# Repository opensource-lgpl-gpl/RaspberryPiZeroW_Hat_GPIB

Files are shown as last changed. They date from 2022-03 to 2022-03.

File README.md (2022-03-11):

# RaspberryPiZeroW_Hat_GPIB
## A $25.66 Dongle 
### Alternative to GPIB National Instrument's USB-GPIB-HS (MSRP: $1,476) and Prologix GPIB-LAN (MSRP: $189.99): 
This is used to standardize old Lab Instruments (Ammeters and Voltage Sources) like the Kiethley Picoammeter and Voltage Source so that a computer can connect wired via USB-A or wirelessly via bluetooth to a Raspberry Pi Zero with Wifi capabilities. 

This contraption RaspberryPiZeroW_Hat_GPIB can deliver results wirelessly via bluetooth or wired via USB-A (Plug) to USB (Plug) so that results can be delivered wirelessly in order to support work-from-home pandemic initiatives. 

This allows the older lab instruments to have the same capabilities as newer more expensive lab instruments that can cost thousands of dollars. 

This side-project used free and open-source tools to show: 
- Free software like KiCAD can completely replace Altium and intra-convertibility between Altium-to-KiCAD. 
- Free software auto-routing tool FreeRoute can replace most of manual PCB design routing. 
- Free software FreeCAD can completely replace SolidWorks, AutoCAD, et cetera (all costly "CAD" software). 

## Why was this created? 
During my time at NASA, I was tasked with getting a Prologix-LAN (MSRP $189.99) to talk to an old lab instrument: 

I was having a hard time connecting to a Prologix GPIB-Lan that was talking to a Kiethley instrument because when I sent the Prologix controller a command to go into "recieve"/"listen" mode, the logic was inverted; what resulted was the Prologix controller started to spew out a lot of data. Then when I wanted the Prologix controller to give me data or in other words, to "talk," the Prologix controller was silenced and went into "recieve"/"listen" mode. 

So I said to myself: "Why would I want to use a GPIB controller that does the exact opposite of what you want it to? Wouldn't that unpredictability potentially compromise valuable results someday when something invariably goes wrong, and you are trying to look for a root-cause?"

To me, this was not rocket science; I scoured the internet and found Thomas Klima's work on Raspberry Pi Model 3's USB-GPIB. 

Link to thesis paper (I studied German at University of Freie-Universitat, Berlin, Germany in 2013): http://elektronomikon.org//Bakkarbeit%20RasPi-GPIB%20Thomas%20Klima.pdf

I worked on this project about 6-8 hours total; most of the time was spent on tool setup and getting used to KiCAD, FreeCAD, and FreeRoute on a Mac machine.

This $25 dongle RaspberryPiZeroW_Hat_GPIB would be placed on every old lab instrument to modernize/"upgrade" it. 

## Bill of Materials from Digikey and OshPark and Raspberry Pi 
### (Total Cost of Materials)
| Part                               | Unit price  | Quantity | Digikey Part No.    | Price    |
| ---------------------------------- | ----------- | -------- | ------------------- | -------- |
| IC TRANSCEIVER HALF 8/8 20DIP      | 3.69        | 1        | SN75160BN           | $3.69    |
| IC TRANSCEIVER HALF 8/8 20SOIC     | 2.74        | 1        | SN75161BDWR         | $2.74    |
| RES ARRAY 5 RES 3.3K OHM 10SIP     | 0.63        | 2        | 4610X-102-332LF     | $1.26    |
| RES ARRAY 9 RES 6.8K OHM 10SIP     | 0.63        | 2        | 4610X-101-682LF     | $1.26    |
| CAP CER 0805 220NF 100V X7R 5%     | 0.31        | 1        | C0805C224J1REC7800  | $0.31    |
| RES 100 OHM 1% 1/4W 0805           | 0.07        | 20       | RNCP0805FTD100R     | $1.40    |
| Oshpark PCB Fab                    | $5.00       | 1        | N/A                 | $5.00    |
| Raspberry Pi   Zero W              | $10.00      | 1        | N/A                 | $10.00   |
|                                    |             |          | **Total:**          | $25.66   |

## PCB design and schematics. 
### Tool used: KiCAD
#### Cost of Tool used: Free, Open-source
KiCAD is a free alternative to more expensive software suites like Altium. 


## FreeRouting Tool to auto-route the PCB
### Tool used: FreeRouting
#### Cost of Tool used: Free, Open-source
I used the open-source and free tool called FreeRouting (https://freerouting.org) to route the PCB and ensure that a mounting bracket would fit. 

The PCB was designed using Free Routing to prevent cross-talk of wires as well as support a FreeCAD-designed mounting bracket. 

What is shown is the schematics taken from KiCAD. 



## Right Angle Mounting Bracket between the Raspberry Pi Zero W and GPIB Rpi Hat. 
### Tool used: FreeCAD
#### Cost of Tool used: Free, Open-source
This is the mounting bracket that was to be 3D printed using my personal 3D Printer from Monoprice. 


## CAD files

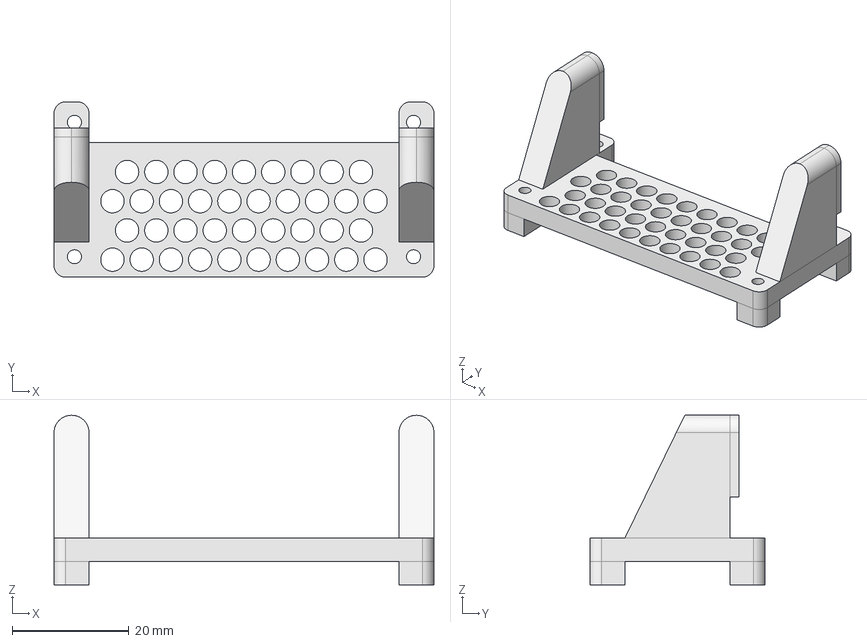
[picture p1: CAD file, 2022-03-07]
Mounting Bracket - FreeCAD/Mounting Bracket.FCStd
65.0 x 30.0 x 29.0 mm

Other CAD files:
Mounting Bracket - FreeCAD/Mounting Bracket.stl

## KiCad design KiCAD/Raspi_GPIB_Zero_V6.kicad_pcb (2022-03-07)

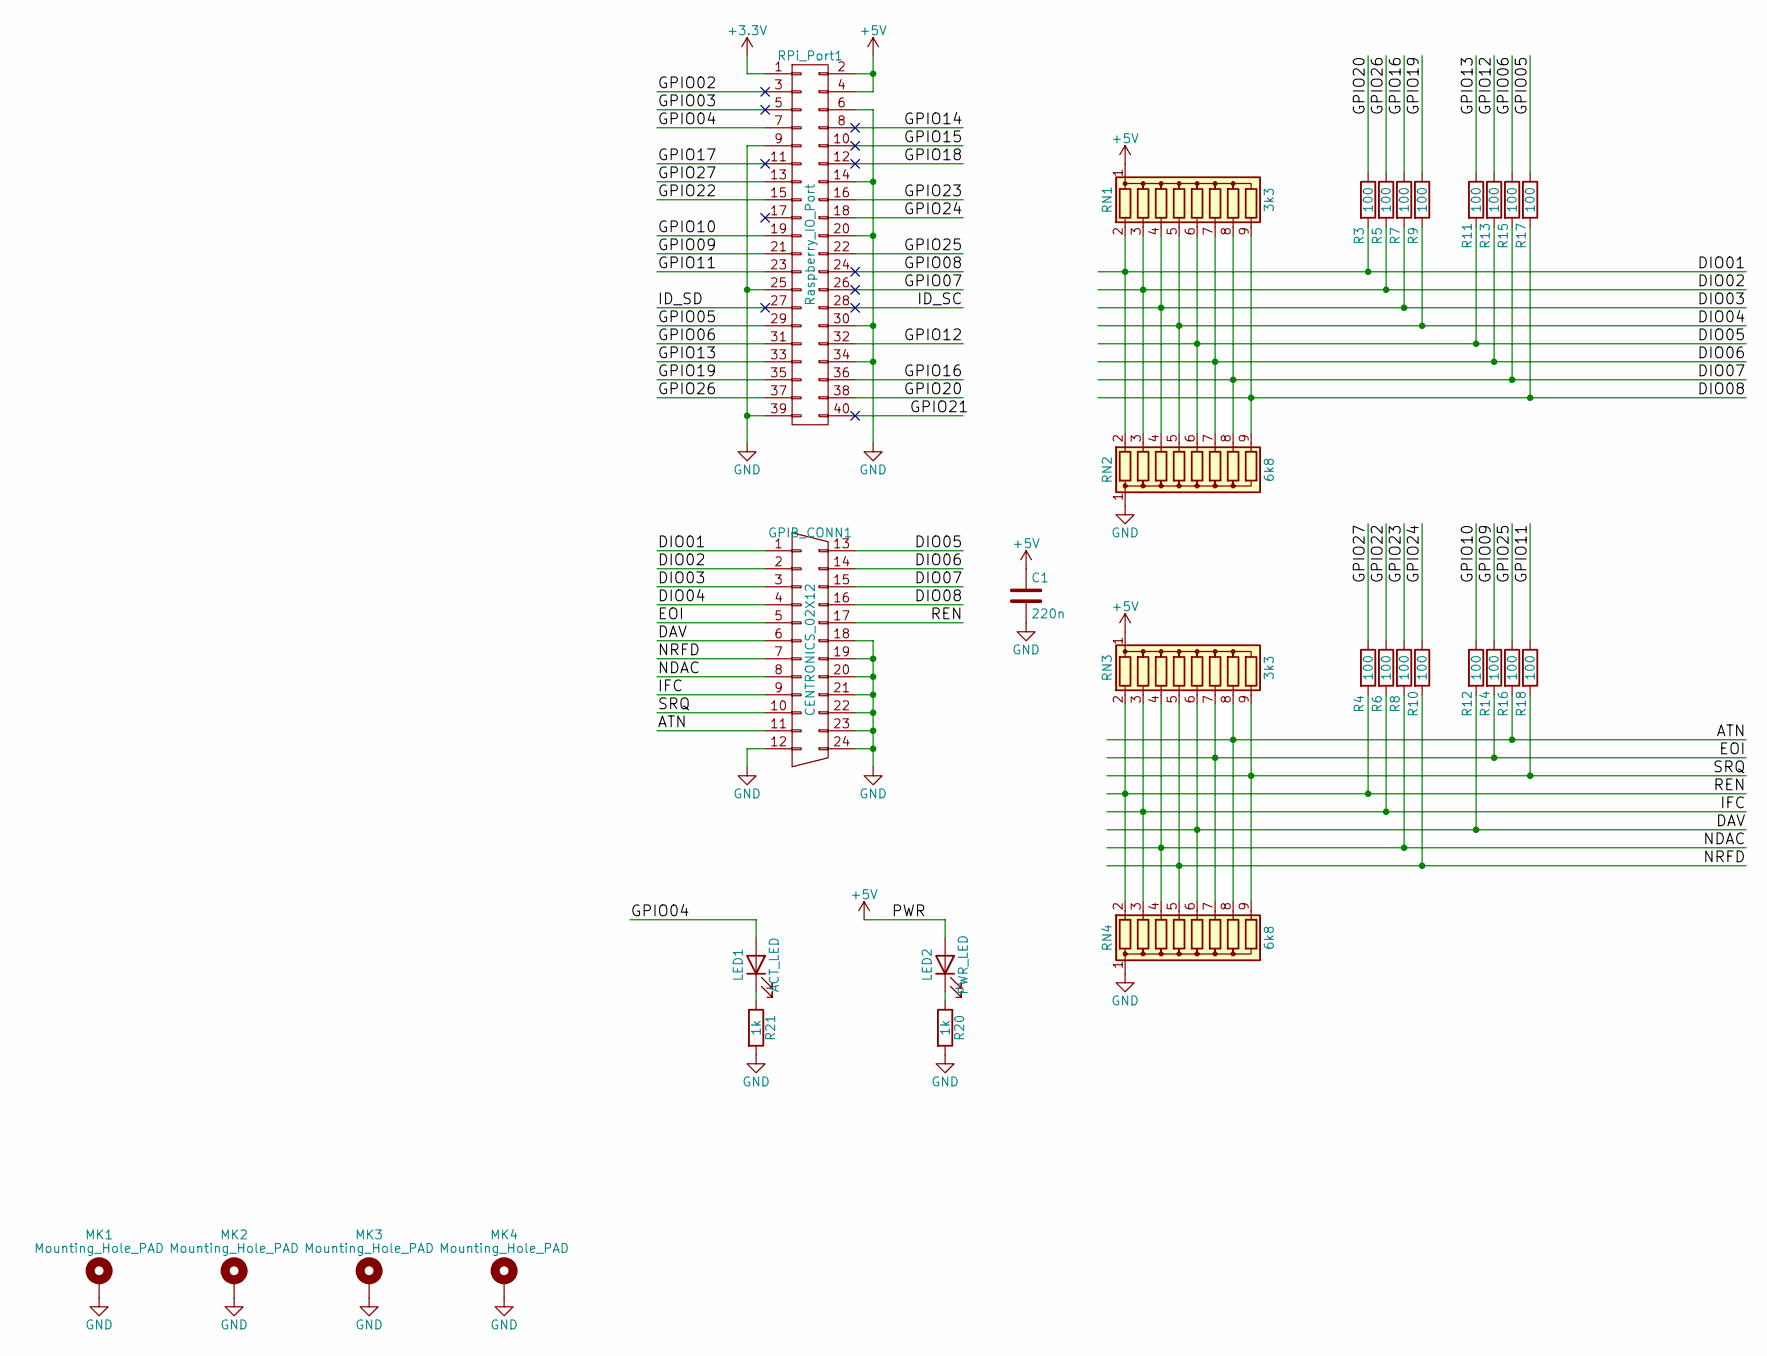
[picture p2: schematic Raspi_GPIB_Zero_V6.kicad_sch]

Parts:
C1: 220n; C_0805_2012Metric
GPIB_CONN1: CENTRONICS_02X12; 112024113R001
LED1: ACT_LED; LED_0805_2012Metric
LED2: PWR_LED; LED_0805_2012Metric
MK1, MK2, MK3, MK4: Mounting_Hole_PAD; MountingHole_2.7mm_M2.5_Pad
R3, R4, R5, R6, R7, R8, R9, R10, R11, R12, R13, R14, R15, R16, R17, R18: 100; R_0805_2012Metric
R20, R21: 1k; R_0805_2012Metric
RN1, RN3: 3k3; Resistor_array_SIP9_3k3
RN2, RN4: 6k8; Resistor_array_SIP9_6k8
RPi_Port1: Raspberry_IO_Port; PinHeader_2x20_P2.54mm_Horizontal

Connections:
+3V3: RPi_Port1.1 (3V3)
+5V: C1.1, LED2.2 (A), RN1.1 (common), RN3.1 (common), RPi_Port1.2 (5V), RPi_Port1.4 (5V)
/ATN: GPIB_CONN1.11, R16.2, RN3.8 (R7), RN4.8 (R7)
/DAV: GPIB_CONN1.6, R12.2, RN3.6 (R5), RN4.6 (R5)
/DIO01: GPIB_CONN1.1, R3.2, RN1.2 (R1), RN2.2 (R1)
/DIO02: GPIB_CONN1.2, R5.2, RN1.3 (R2), RN2.3 (R2)
/DIO03: GPIB_CONN1.3, R7.2, RN1.4 (R3), RN2.4 (R3)
/DIO04: GPIB_CONN1.4, R9.2, RN1.5 (R4), RN2.5 (R4)
/DIO05: GPIB_CONN1.13, R11.2, RN1.6 (R5), RN2.6 (R5)
/DIO06: GPIB_CONN1.14, R13.2, RN1.7 (R6), RN2.7 (R6)
/DIO07: GPIB_CONN1.15, R15.2, RN1.8 (R7), RN2.8 (R7)
/DIO08: GPIB_CONN1.16, R17.2, RN1.9 (R8), RN2.9 (R8)
/EOI: GPIB_CONN1.5, R14.2, RN3.7 (R6), RN4.7 (R6)
/GPIO02: RPi_Port1.3 (GPIO2)
/GPIO03: RPi_Port1.5 (GPIO3)
/GPIO04: LED1.2 (A), RPi_Port1.7 (GPIO4)
/GPIO05: R17.1, RPi_Port1.29 (GPIO05)
/GPIO06: R15.1, RPi_Port1.31 (GPIO06)
/GPIO07: RPi_Port1.26 (GPIO07)
/GPIO08: RPi_Port1.24 (GPIO08)
/GPIO09: R14.1, RPi_Port1.21 (GPIO10)
/GPIO10: R12.1, RPi_Port1.19 (GPIO09)
/GPIO11: R18.1, RPi_Port1.23 (GPIO11)
/GPIO12: R13.1, RPi_Port1.32 (GPIO12)
/GPIO13: R11.1, RPi_Port1.33 (GPIO13)
/GPIO14: RPi_Port1.8 (GPIO14)
/GPIO15: RPi_Port1.10 (GPIO15)
/GPIO16: R7.1, RPi_Port1.36 (GPIO16)
/GPIO17: RPi_Port1.11 (GPIO17)
/GPIO18: RPi_Port1.12 (GPIO18)
/GPIO19: R9.1, RPi_Port1.35 (GPIO19)
/GPIO20: R3.1, RPi_Port1.38 (GPIO20)
/GPIO21: RPi_Port1.40 (GPIO21)
/GPIO22: R6.1, RPi_Port1.15 (GPIO22)
/GPIO23: R8.1, RPi_Port1.16 (GPIO23)
/GPIO24: R10.1, RPi_Port1.18 (GPIO24)
/GPIO25: R16.1, RPi_Port1.22 (GPIO25)
/GPIO26: R5.1, RPi_Port1.37 (GPIO26)
/GPIO27: R4.1, RPi_Port1.13 (GPIO27)
/ID_SC: RPi_Port1.28 (ID_SC)
/ID_SD: RPi_Port1.27 (ID_SD)
/IFC: GPIB_CONN1.9, R6.2, RN3.3 (R2), RN4.3 (R2)
/NDAC: GPIB_CONN1.8, R8.2, RN3.4 (R3), RN4.4 (R3)
/NRFD: GPIB_CONN1.7, R10.2, RN3.5 (R4), RN4.5 (R4)
/REN: GPIB_CONN1.17, R4.2, RN3.2 (R1), RN4.2 (R1)
/SRQ: GPIB_CONN1.10, R18.2, RN3.9 (R8), RN4.9 (R8)
GND: C1.2, GPIB_CONN1.12, GPIB_CONN1.18, GPIB_CONN1.19, GPIB_CONN1.20, GPIB_CONN1.21, GPIB_CONN1.22, GPIB_CONN1.23, GPIB_CONN1.24, MK1.1, MK2.1, MK3.1, MK4.1, R20.2, R21.2, RN2.1 (common), RN4.1 (common), RPi_Port1.6 (GND), RPi_Port1.9 (GND), RPi_Port1.14 (GND), RPi_Port1.20 (GND), RPi_Port1.25 (GND), RPi_Port1.30 (GND), RPi_Port1.34 (GND), RPi_Port1.39 (GND)
unnamed: LED1.1 (K), R21.1
unnamed: LED2.1 (K), R20.1

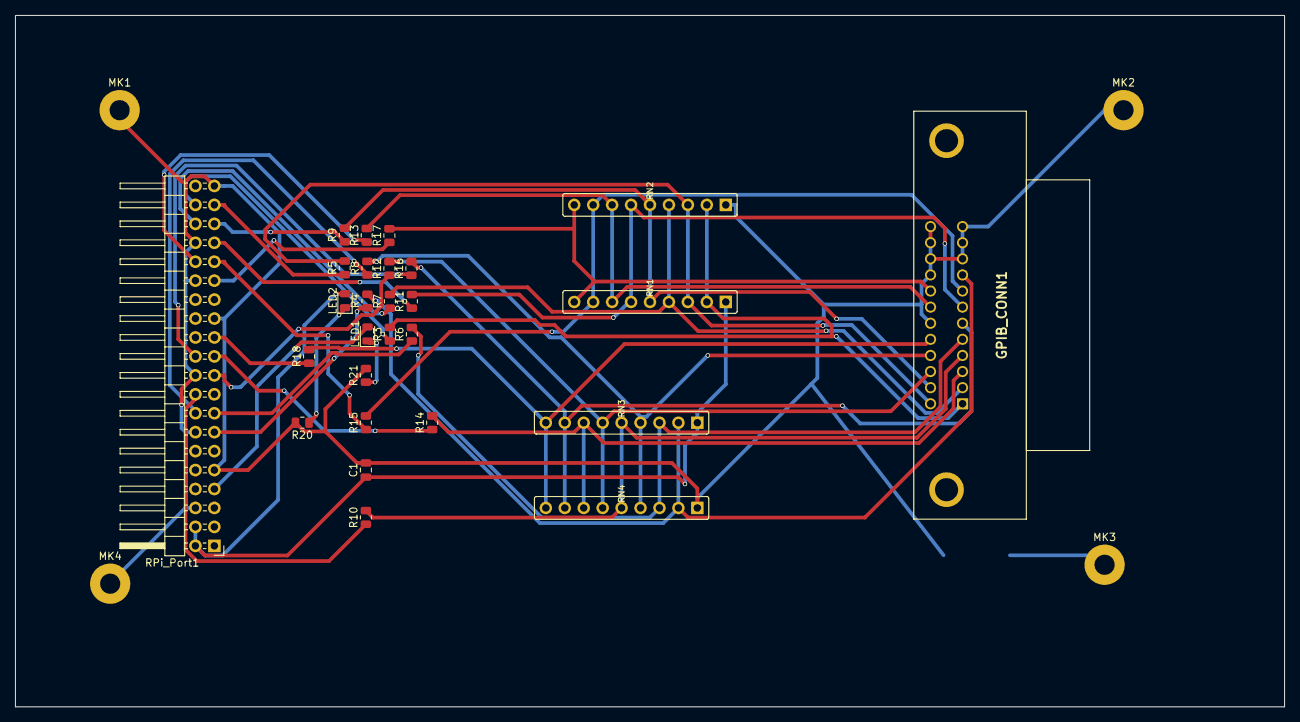
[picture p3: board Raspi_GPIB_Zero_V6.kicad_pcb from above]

Board: 2 copper layers, 170.2 x 92.7 mm, 31 parts (0 on the bottom side), 37 nets.

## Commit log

2022-03-07 adding to master repository
    [Mounting Bracket.FCStd, Mounting Bracket.stl, Raspi_GPIB_Zero_V6.dsn, Raspi_GPIB_Zero_V6.kicad_pcb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]
2022-03-08 Update README.md
    Adding time when I made the GPIB Hat for the raspberry pi.
